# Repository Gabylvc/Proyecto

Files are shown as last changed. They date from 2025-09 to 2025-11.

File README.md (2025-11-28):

# 🧬 Fundamentos de Biodiseño - REMOOV

Este proyecto forma parte del curso **Fundamentos de Biodiseño** del grupo 11.  
A continuación, se presentan los integrantes del equipo de trabajo.

---

##  Integrantes

- **Goran Acurio Cabrera**  - goran.acurio@upch.pe
- **Gabriela Barrios** - gabriela.barrios@upch.pe
- **Jorge Briceño Hijar** - jorge.briceno@upch.pe
- **Marco Baltazar** - marco.baltazar@upch.pe
- **Camila Araujo** - camila.araujo@upch.pe
- **Katherin Berrio** - katherin.berrio@upch.pe

---

## Grupo de trabajo

| Grupo de trabajo|
|--------------|
| foto |

---

## Temática

En este proyecto nos enfocamos en proporcionar una alternativa de movimiento en silla de ruedas para usuarios con lesiones medulares que cuentan con movilidad parcial en las extremidades superiores
|--------------|
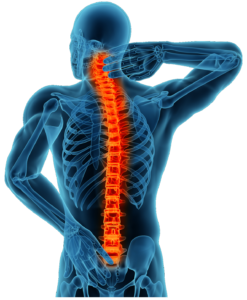
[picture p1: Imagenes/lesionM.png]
foto
|  |
---
## Problemática
El usuario sufrió una lesión medular C4 incompleta tipo C como producto de un accidente automovilístico. A raíz de esta lesión  la movilidad del paciente se encuentra comprometida, dependiendo completamente de una silla de ruedas para desplazarse. Sus extremidades inferiores no tienen rango de movilidad alguna, sin embargo tiene cierto rango de movimiento en sus brazos, lo que llevó a pensar que sería capaz de remar su silla de ruedas, sin embargo al no poder cerrar los dedos de las manos ni poder retraer completamente los brazos se le hizo imposible, por lo que ahora depende completamente de sus cuidadora principal.
## Justificación
Las sillas de ruedas convencionales son ampliamente utilizadas gracias a su bajo costo, disponibilidad y accesibilidad. Sin embargo, existen usuarios con limitaciones en su capacidad motora que requieren asistencia para desplazarse perdiendo su autonomía y desarrollo en actividades cotidianas.
El esfuerzo físico requerido para propulsar una silla mecánica puede resultar excesivo y puede llegar a generar fatiga muscular, lesiones por el sobreuso y desgaste prematuro en articulaciones; muestra de esto es el hecho de que, entre 31-73% de la población con lesiones en la médula espinal reportan dolor de hombro, muchas veces crónico [1]. A ello se le suma la necesidad recurrente de un acompañante, lo que restringe la independencia del usuario y limita su integración plena en la sociedad. 
En el caso específico de nuestro paciente, su limitada movilidad y fuerza en los brazos hace casi imposible el buen manejo de su silla de ruedas, necesidad en la cual nos enfocaremos.
En tal sentido, es necesario buscar alternativas para las sillas de ruedas convencionales, ya que en el mercado ya existen dispositivos motorizados; sin embargo, suelen implicar un costo elevado, dificultades en el mantenimiento y poca adaptabilidad a contextos con recursos limitados.
## Solución
Sistema de propulsión asistida basada en una palanca conectada al sobrearo de la silla de ruedas.
|--------------|
| foto |
---

## Referencias
[1] A. Liampas, P. Neophytou, M. Sokratous, G. Varrassi, C. Ioannou, G. M. Hadjigeorgiou, and P. Zis, “Musculoskeletal Pain Due to Wheelchair Use: A Systematic Review and Meta-Analysis,” Pain Ther., vol. 10, no. 2, pp. 973–984, Dec. 2021, doi: 10.1007/s40122-021-00294-5.

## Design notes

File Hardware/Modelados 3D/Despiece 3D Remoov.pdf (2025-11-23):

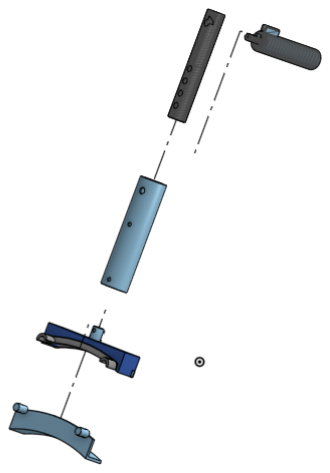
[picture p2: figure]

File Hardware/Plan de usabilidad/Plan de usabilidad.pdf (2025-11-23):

Plan de usabilidad:
a. Contexto de uso
¿Quién es el usuario?
El dispositivo está dirigido a pacientes con lesiones medulares graves que conservan movilidad parcial en las extremidades superiores; además, se cuenta con funciones de monitoreo dirigidas al cuidador y al terapeuta.
¿Cómo se utiliza el dispositivo?
El dispositivo debe acoplarse al sobre aro de la silla de ruedas y ajustarse a ella; después, la altura de la palanca debe ajustarse a la altura óptima para el agarre del usuario. Una vez realizados estos pasos, la electrónica del dispositivo se enciende mediante un switch ubicado en la caja electrónica. El movimiento de la silla de ruedas se logra mediante el movimiento de los brazos del usuario en forma de remo hacia adelante y hacia atrás, de esta manera se logra hacer fricción con el sobre aro y propulsar la silla hacia adelante; para realizar el cambio de adelante hacia atrás, se utiliza un cable bowden, el cual cambia el sentido con un movimiento de giro del mango del usuario.
La aplicación se conecta mediante bluetooth al sistema electrónico del dispositivo; una vez conectado, la información en forma de gráficas de la presión ejercida y el ángulo de movimiento se presentarán en la pantalla.
¿Dónde se utilizará el dispositivo?
El dispositivo está diseñado para que el paciente pueda utilizarlo en cualquier lugar donde se encuentre, ya sea en su hogar, en el hospital o en la calle. Por lo tanto, su frecuencia de uso también es elevada, ya que cubre todos los momentos en los cuales el paciente utiliza su silla de ruedas.

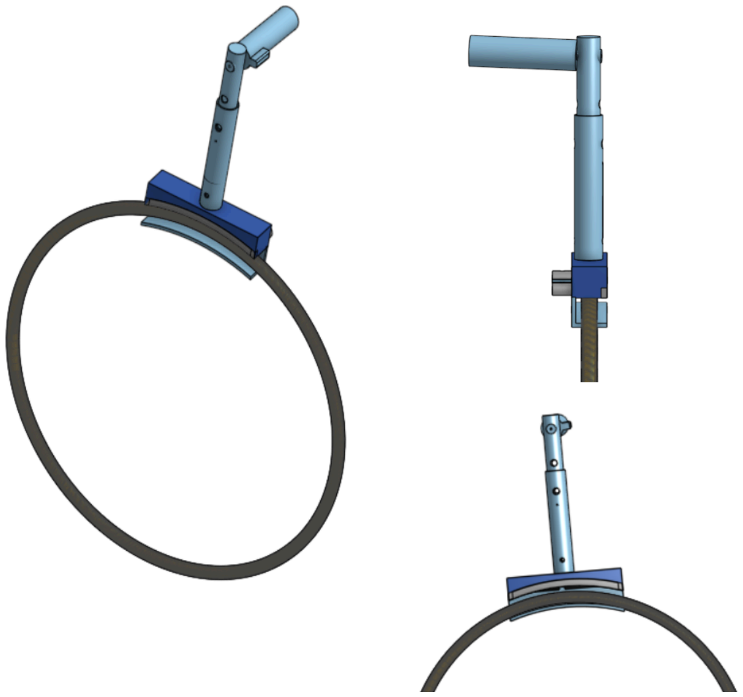
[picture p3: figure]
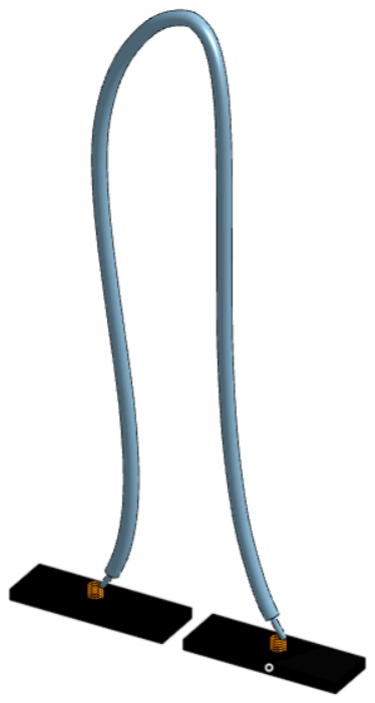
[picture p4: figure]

b. Perfil del usuario

–Qué es:
El usuario es un hombre de 30 años con una lesión medular cervical C3–C4 (AIS C) provocada por un accidente de tránsito. Desde entonces, presenta parálisis total en las piernas y fuerza muy limitada en los brazos. Su movilidad activa está reducida en las cuatro extremidades, aunque conserva sensibilidad hasta el nivel C4. En los brazos apenas logra fuerza entre 4/5 y 1/5, lo que le dificulta propulsar una silla de ruedas convencional. Aun así, mantiene plena conciencia, comprensión y orientación, lo que le permite participar activamente en su proceso de rehabilitación

– Qué hacer:
El paciente necesita un sistema que le permita desplazarse con menor esfuerzo y mayor seguridad. Para ello se propone una palanca de asistencia basada en la patente Wheelchair Propulsion Assist Device (US11590039B1), que se instala sobre el aro de la rueda para reducir el torque necesario y aprovechar la fuerza residual de los brazos. Además, se integra electrónica al diseño: un sensor de fuerza para medir el esfuerzo de propulsión, un giroscopio para registrar la estabilidad del movimiento y una alerta automática conectada a una aplicación móvil que avisa si el usuario sufre una caída o pierde el equilibrio. Este sistema busca facilitar la movilidad, prevenir lesiones en los hombros y aumentar la independencia en sus actividades diarias. [1]

– Qué evidencia debe incluir:
El caso clínico proporciona la información principal sobre el estado físico, diagnóstico y metas de rehabilitación del paciente, que sirven de base para el diseño del dispositivo.La patente US11590039B1 respalda el principio mecánico del sistema de palanca y demuestra su aplicabilidad en sillas de ruedas. Asimismo, estudios científicos como el de Requejo muestran que los mecanismos de palanca reducen la carga muscular en los hombros de personas con lesión medular. [2]

En conjunto, la información clínica, la evidencia técnica y el soporte científico justifican el desarrollo de una palanca asistida con monitoreo electrónico, adaptada a un usuario con severas limitaciones motoras pero con plena capacidad cognitiva, que busca recuperar autonomía y seguridad en su vida cotidiana.

c. Análisis de tareas
Tareas | ¿Crítica? | Riesgos / Consecuencias en caso de error | Justificación
Montar y fijar el dispositivo a la silla de ruedas | Sí | Un desacople mediante el uso de la silla, puede generar una pérdida de control, caída e incluso lesión | Necesidad de un retrofit seguro y puntos de fijación fiables, puesto que un montaje inadecuado compromete la estabilidad y seguridad del usuario [1] [3]

Ajustar y asegurar el agarre (mango) | Sí | Si la mano resbala o se suelta conlleva una pérdida de propulsión y control | Necesario para usuarios con espasticidad o bajo rango de movimiento para transferir fuerza y movimiento a la silla (uso de agarre ergonómico) [3]
Selección de modo (avance / retroceso) | Sí | Movimiento inesperado en el mango o selector mal posicionado ocasionaría colisiones o pérdida de control | Necesidad de definir posiciones de manejo de la silla para evitar movimientos indeseados [1] [4]
Activar freno antes de sentarse / desmontar | Sí | Rodado involuntario provocaría una posible caída del usuario o daños en el dispositivo | Necesidad de mecanismos de bloqueo o freno para evitar rollaway [1] [3] [4]
Realizar gesto de propulsión (remada) | No/ Algunos casos | Mala técnica ocasionaría espasticidad, fatiga, dolor en hombro e incluso riesgo de lesión por sobreuso | Necesidad de un diseño ergonómico para evitar daños por repetición con técnica inadecuada [1] [4]
Monitorear señales / sensores (encender sistema, mantener registro y vigilar alertas) | Sí | Si no hay registro de eventos o alertas, no existe un seguimiento del movimiento de la silla y posibles fallas | Necesidad de detectar situaciones de peligro y un seguimiento del movimiento de la silla para la seguridad del usuario [4]
Desmontaje y almacenamiento | No/ Algunos casos | Un almacenamiento incorrecto provocaría daños en piezas, por lo que el próximo uso sería inseguro | Buenas prácticas de mantenimiento reducen fallas en uso posterior [1] [4]
d. Criterios de éxito:
Criterio | Alcance de objetivo | Método de evaluación
Eficacia | El ≧ 95% de tareas completadas sin error. | Se completó el prototipado electrónico y el modelado en 3D con un correcto indicador de rendimiento. [5]

Eficiencia | < 1 minuto en la inicialización y detección de parámetros. | Cronometrado en las pruebas de desarrollo con un tiempo adecuado para un correcto desarrollo intuitivo. [5]
Satisfacción | Por definir en pruebas con el usuario. | Serie de preguntas durante el uso del dispositivo y evaluado con una métrica SUS [6].
Seguridad | 0 colisiones y fallos críticos | No hubo incidentes durante las pruebas del dispositivo.
Accesibilidad | Contraste ≧ 80%, íconos > 1cm | Se verificó un contraste del 80% y una manipulación sencilla en la aplicación móvil.

Referencias
[1] J. W. Britz, “Wheelchair propulsion assist device,” U.S. Patent 11,590,039 B1, Feb. 28, 2023. [En línea]. Disponible: https://patents.google.com/patent/US11590039B1/en
[2] P. S. Requejo et al., “Shoulder muscular demand during lever-activated vs. pushrim wheelchair propulsion in persons with spinal cord injury,” Arch. Phys. Med. Rehabil., vol. 89, no. 8, pp. 1380–1387, 2008. Available:
https://pubmed.ncbi.nlm.nih.gov/19086715/
[3] D. Zondervan, D. Reinkensmeyer y B. Smith, “Lever-operated wheelchair,” U.S. Patent
9,597,241 | B2, | 21 | de | marzo | de | 2017. | [En | línea]. | Disponible:
https://patents.google.com/patent/US9597241B2/en
[4] P. Bitzer, B. Stumpp, “Dispositivo de asistencia para desplazamiento de silla de ruedas,”
Patente | Española | ES | 2 | 438 | 816 | T3, | 2014. | [En | línea]. | Disponible:
https://patents.google.com/patent/ES2438816T3/es?oq=ES2438816T3
[5] J. Nielsen, Usability Engineering. San Francisco: Academic Press, 1994.
[6] J. Brooke, “SUS: A quick and dirty usability scale,” in Usability Evaluation in Industry, P.
W. | Jordan, | B. | Thomas, | B. | A. | Weerdmeester, | and | I. | L.
https://www.researchgate.net/publication/228593520_SUS_A_quick_and_dirty_usability_sca le (https://www.researchgate.net/publication/228593520_SUS_A_quick_and_dirty_usability_scale)

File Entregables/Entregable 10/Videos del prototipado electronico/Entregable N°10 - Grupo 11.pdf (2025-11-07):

### Entregable N°10 - Grupo 11

Prototipado electrónico:

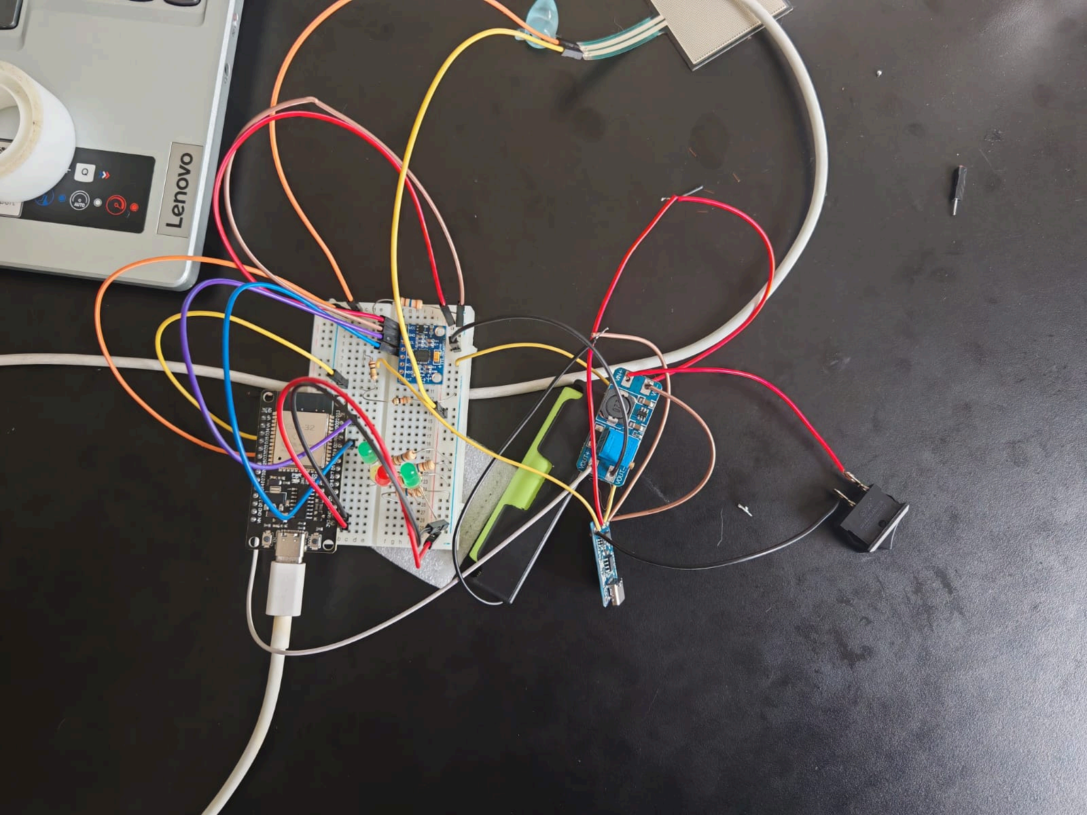
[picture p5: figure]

Videos de funcionamiento:
https://github.com/Gabylvc/Proyecto/tree/main/Entregables/Entregable%2010/Videos %20del%20prototipado%20electronico (https://github.com/Gabylvc/Proyecto/tree/main/Entregables/Entregable%2010/Videos%20del%20prototipado%20electronico)

Animación 3D:
https://drive.google.com/file/d/1b3KnyuPQWc3HMV8ianJPKPj2rIHMH49K/view?usp=drive_link (https://drive.google.com/file/d/1b3KnyuPQWc3HMV8ianJPKPj2rIHMH49K/view?usp=drive_link)

Despiece 3D:

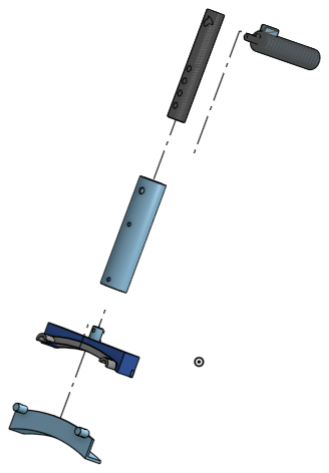
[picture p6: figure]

Plan de usabilidad:
a. Contexto de uso
¿Quién es el usuario?
El dispositivo está dirigido a pacientes con lesiones medulares graves que conservan movilidad parcial en las extremidades superiores; además, se cuenta con funciones de monitoreo dirigidas al cuidador y al terapeuta.
¿Cómo se utiliza el dispositivo?
El dispositivo debe acoplarse al sobre aro de la silla de ruedas y ajustarse a ella; después, la altura de la palanca debe ajustarse a la altura óptima para el agarre del usuario. Una vez realizados estos pasos, la electrónica del dispositivo se enciende mediante un switch ubicado en la caja electrónica. El movimiento de la silla de ruedas se logra mediante el movimiento de los brazos del usuario en forma de remo hacia adelante y hacia atrás, de esta manera se logra hacer fricción con el sobre aro y propulsar la silla hacia adelante; para realizar el cambio de adelante hacia atrás, se utiliza un cable bowden, el cual cambia el sentido con un movimiento de giro del mango del usuario.

La aplicación se conecta mediante bluetooth al sistema electrónico del dispositivo; una vez conectado, la información en forma de gráficas de la presión ejercida y el ángulo de movimiento se presentarán en la pantalla.
¿Dónde se utilizará el dispositivo?
El dispositivo está diseñado para que el paciente pueda utilizarlo en cualquier lugar donde se encuentre, ya sea en su hogar, en el hospital o en la calle. Por lo tanto, su frecuencia de uso también es elevada, ya que cubre todos los momentos en los cuales el paciente utiliza su silla de ruedas.


b. Perfil del usuario

–Qué es:


El usuario es un hombre de 30 años con una lesión medular cervical C3–C4 (AIS C) provocada por un accidente de tránsito. Desde entonces, presenta parálisis total en las piernas y fuerza muy limitada en los brazos. Su movilidad activa está reducida en las cuatro extremidades, aunque conserva sensibilidad hasta el nivel C4. En los brazos apenas logra fuerza entre 4/5 y 1/5, lo que le dificulta propulsar una silla de ruedas convencional. Aun así, mantiene plena conciencia, comprensión y orientación, lo que le permite participar activamente en su proceso de rehabilitación

– Qué hacer:
El paciente necesita un sistema que le permita desplazarse con menor esfuerzo y mayor seguridad. Para ello se propone una palanca de asistencia basada en la patente Wheelchair Propulsion Assist Device (US11590039B1), que se instala sobre el aro de la rueda para reducir el torque necesario y aprovechar la fuerza residual de los brazos. Además, se integra electrónica al diseño: un sensor de fuerza para medir el esfuerzo de propulsión, un giroscopio para registrar la estabilidad del movimiento y una alerta automática conectada a una aplicación móvil que avisa si el usuario sufre una caída o pierde el equilibrio. Este sistema busca facilitar la movilidad, prevenir lesiones en los hombros y aumentar la independencia en sus actividades diarias. [1]

– Qué evidencia debe incluir:
El caso clínico proporciona la información principal sobre el estado físico, diagnóstico y metas de rehabilitación del paciente, que sirven de base para el diseño del dispositivo.La patente US11590039B1 respalda el principio mecánico del sistema de palanca y demuestra su aplicabilidad en sillas de ruedas. Asimismo, estudios científicos como el de Requejo muestran que los mecanismos de palanca reducen la carga muscular en los hombros de personas con lesión medular. [2]

En conjunto, la información clínica, la evidencia técnica y el soporte científico justifican el desarrollo de una palanca asistida con monitoreo electrónico, adaptada a un usuario con severas limitaciones motoras pero con plena capacidad cognitiva, que busca recuperar autonomía y seguridad en su vida cotidiana.

c. Análisis de tareas
Tareas | ¿Crítica? | Riesgos / Consecuencias en caso de error | Justificación
Montar y fijar el dispositivo a la silla de ruedas | Sí | Un desacople mediante el uso de la silla, puede generar una pérdida de control, caída e incluso lesión | Necesidad de un retrofit seguro y puntos de fijación fiables, puesto que un montaje inadecuado compromete la estabilidad y seguridad del usuario [1] [3]
Ajustar y asegurar el agarre (mango) | Sí | Si la mano resbala o se suelta conlleva una pérdida de propulsión y control | Necesario para usuarios con espasticidad o bajo rango de movimiento para transferir fuerza y movimiento a la silla (uso de agarre ergonómico) [3]
Selección de modo (avance / retroceso) | Sí | Movimiento inesperado en el mango o selector mal posicionado ocasionaría colisiones o pérdida de control | Necesidad de definir posiciones de manejo de la silla para evitar movimientos indeseados [1] [4]
Activar freno antes de sentarse / desmontar | Sí | Rodado involuntario provocaría una posible caída del usuario o daños en el dispositivo | Necesidad de mecanismos de bloqueo o freno para evitar rollaway [1] [3] [4]

Realizar gesto de propulsión (remada) | No/ Algunos casos | Mala técnica ocasionaría espasticidad, fatiga, dolor en hombro e incluso riesgo de lesión por sobreuso | Necesidad de un diseño ergonómico para evitar daños por repetición con técnica inadecuada [1] [4]
Monitorear señales / sensores (encender sistema, mantener registro y vigilar alertas) | Sí | Si no hay registro de eventos o alertas, no existe un seguimiento del movimiento de la silla y posibles fallas | Necesidad de detectar situaciones de peligro y un seguimiento del movimiento de la silla para la seguridad del usuario [4]
Desmontaje y almacenamiento | No/ Algunos casos | Un almacenamiento incorrecto provocaría daños en piezas, por lo que el próximo uso sería inseguro | Buenas prácticas de mantenimiento reducen fallas en uso posterior [1] [4]
d. Criterios de éxito:
Criterio | Alcance de objetivo | Método de evaluación
Eficacia | El ≧ 95% de tareas completadas sin error. | Se completó el prototipado electrónico y el modelado en 3D con un correcto indicador de rendimiento. [5]
Eficiencia | < 1 minuto en la inicialización y detección de parámetros. | Cronometrado en las pruebas de desarrollo con un tiempo adecuado para un correcto desarrollo intuitivo. [5]
Satisfacción | Por definir en pruebas con el usuario. | Serie de preguntas durante el uso del dispositivo y evaluado con una métrica SUS [6].
Seguridad | 0 colisiones y fallos críticos | No hubo incidentes durante las pruebas del dispositivo.
Accesibilidad | Contraste ≧ 80%, íconos > 1cm | Se verificó un contraste del 80% y una manipulación sencilla en la aplicación móvil.

Referencias
[1] J. W. Britz, “Wheelchair propulsion assist device,” U.S. Patent 11,590,039 B1, Feb. 28, 2023. [En línea]. Disponible: https://patents.google.com/patent/US11590039B1/en
[2] P. S. Requejo et al., “Shoulder muscular demand during lever-activated vs. pushrim wheelchair propulsion in persons with spinal cord injury,” Arch. Phys. Med. Rehabil., vol. 89, no. 8, pp. 1380–1387, 2008. Available:
https://pubmed.ncbi.nlm.nih.gov/19086715/
[3] D. Zondervan, D. Reinkensmeyer y B. Smith, “Lever-operated wheelchair,” U.S. Patent
9,597,241 | B2, | 21 | de | marzo | de | 2017. | [En | línea]. | Disponible:
https://patents.google.com/patent/US9597241B2/en
[4] P. Bitzer, B. Stumpp, “Dispositivo de asistencia para desplazamiento de silla de ruedas,”
Patente | Española | ES | 2 | 438 | 816 | T3, | 2014. | [En | línea]. | Disponible:
https://patents.google.com/patent/ES2438816T3/es?oq=ES2438816T3
[5] J. Nielsen, Usability Engineering. San Francisco: Academic Press, 1994.
[6] J. Brooke, “SUS: A quick and dirty usability scale,” in Usability Evaluation in Industry, P.
W. | Jordan, | B. | Thomas, | B. | A. | Weerdmeester, | and | I. | L.
https://www.researchgate.net/publication/228593520_SUS_A_quick_and_dirty_usability_sca le (https://www.researchgate.net/publication/228593520_SUS_A_quick_and_dirty_usability_scale)

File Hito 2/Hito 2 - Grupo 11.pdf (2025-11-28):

RE-

# MOOVE

P R E S E N T A C I Ó N

Presentado por: GRUPO 11
FUNDAMENTOS DEL BIODISEÑO

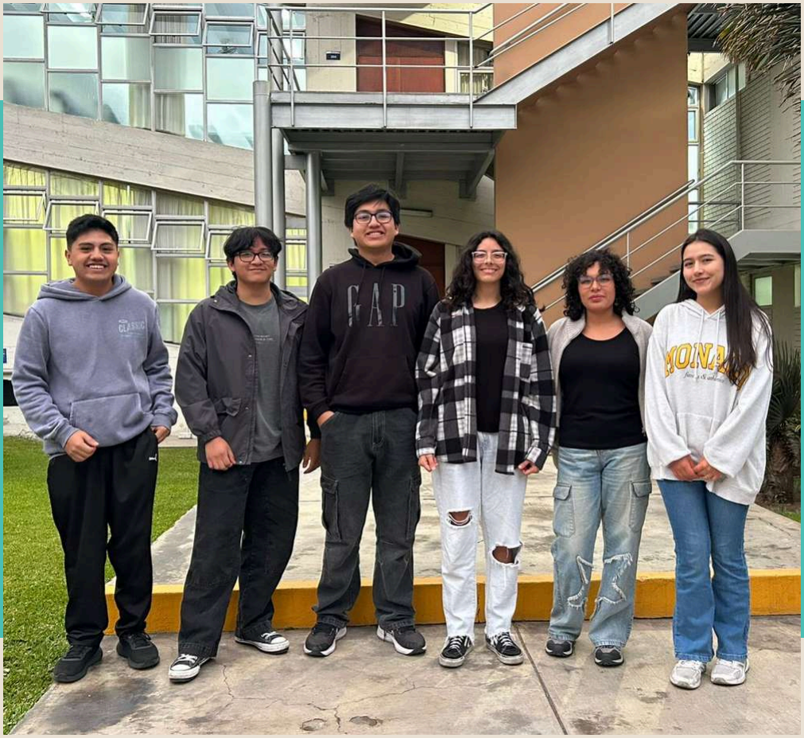
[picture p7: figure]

# El equipo

Goran Acurio (Coordinador y E.

electrónica)
Camila Araujo (E. de Mecanismos) Marco Baltazar (E. de Manufactura

Digital)
Gabriela Barrios (E. de Ensamblado e

integración)
Katherin Berrio (E. de Mecanismos) Jorge Briceño (E. de Diseño Digital)

01

# Problemática y Solución

# Lesión Medular Cervical C3–C5

### Consecuencia:

Tetraparesia → fuerza limitada en hombros, sin control en manos/piernas.

### Zona afectada:

Médula espinal cervical

### Implicaciones:

Pérdida parcial de movilidad y sensibilidad en brazos y piernas.

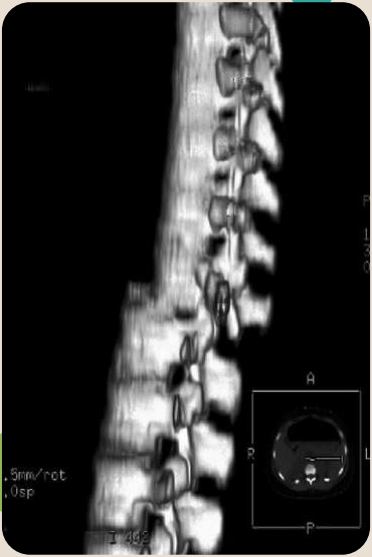
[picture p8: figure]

Lesión Medular Cervical C3–C5: https://www.fisioterapianeurologica.es/patologias/lesion-medular/

# Estadísticas

personas sufren una lesión medular

El INR indica que alrededor del 60 % de los casos se deben a a accidentes vehiculares [2]

Según la Organización Mundial de la Salud...

de casos corresponden 62% a lesiones cervicales. [1]

250000 - 500000

Otras

Accidentes de
tránsito

Caídas

60%

25%

5%

En el Perú...

1

2

3

# Análisis de caso

Problema clínico y funcional:

Fuerza parcial en hombros y ausencia de movimiento en
manos
Dificultad | severa | para
propulsar una silla de ruedas. No puede desplazarse por sí mismo, depende de terceros.

Necesidad del usuario:

Mover la silla con menor esfuerzo y mayor comodidad en su día a día Recibe manejo integral de rehabilitación, incluyendo fisioterapia para mantener el tono muscular; sin embargo, requiere logra propulsión funcional independiente.

Impacto esperado de la solución:

Recuperar autonomía en movilidad. Reducir la dependencia de cuidadores. Facilitar su participación activa en su entorno social, educativo y laboral.

Imagen del caso clínico.
Fuente: Muñoz Maldonado,
C. (2024). Presentación de clase, Rehabilitación.

Análisis biomecánico de propulsión en silla de ruedas.
https://www.frontiersin.org/journals/rehabilit ationsciences/articles/10.3389/fresc.2022.863093 /full

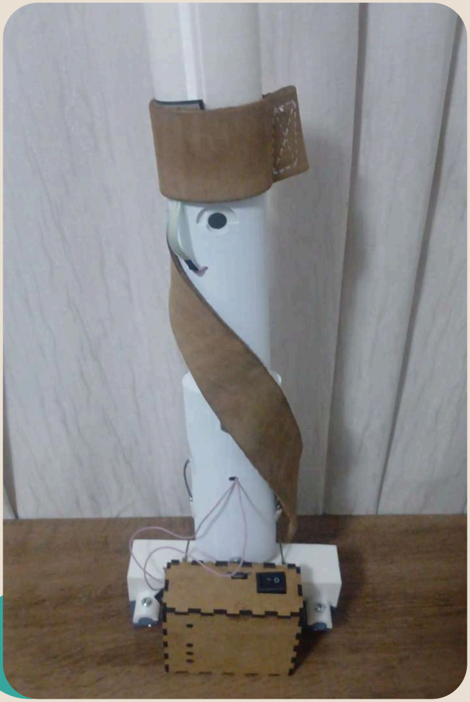
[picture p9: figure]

# SOLUCIÓN ENCONTRADA:

Acoplar el dispositivo en la silla de ruedas Seleccionar el modo avance/retroceso y encender la electrónica si es necesario tomar datos
Realizar movimientos de remo

## “Sistema de propulsión en forma de palanca acoplado al sobrearo

”

02

# Boceto y modelado 3D

# B O C ET O S INI C I A LES

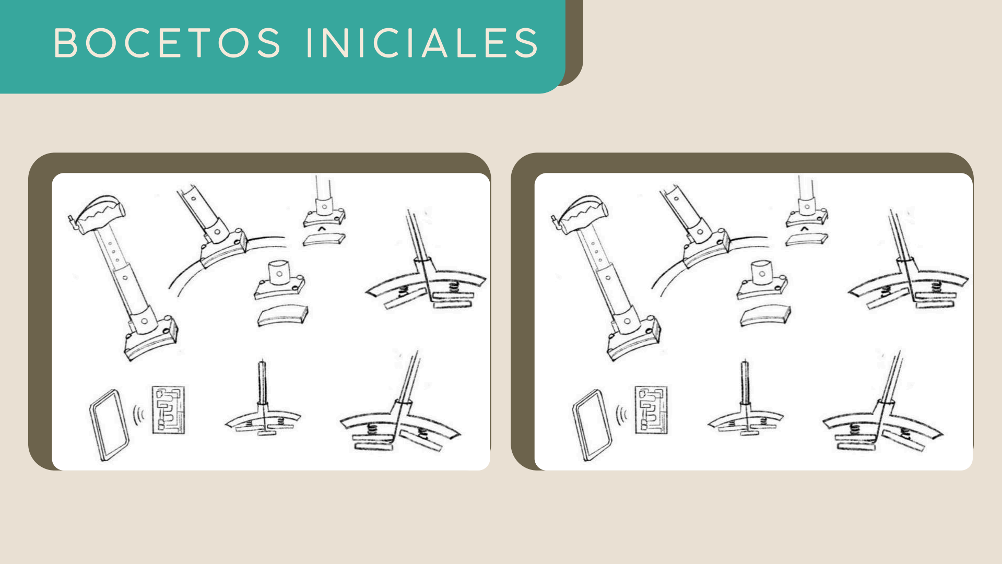
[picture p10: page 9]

# PRIMER A S PIEZ A S

## C A J A DE ELE C TR O NI C A

## P A L ANC A RE GUL A BLE

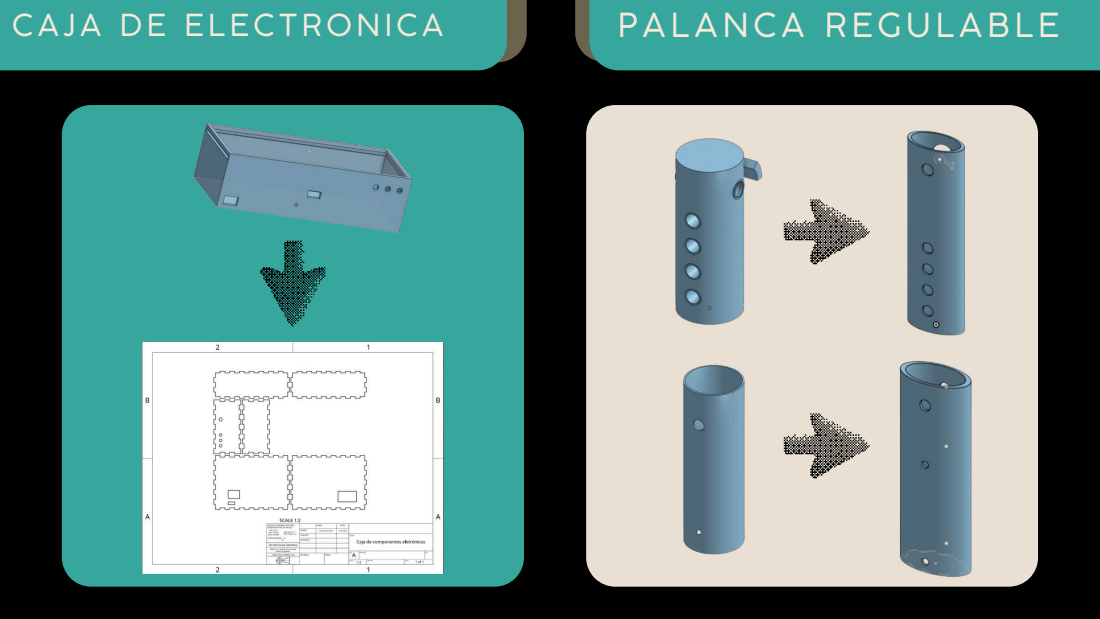
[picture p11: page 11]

MA R C O SUPERI O R | MANG O

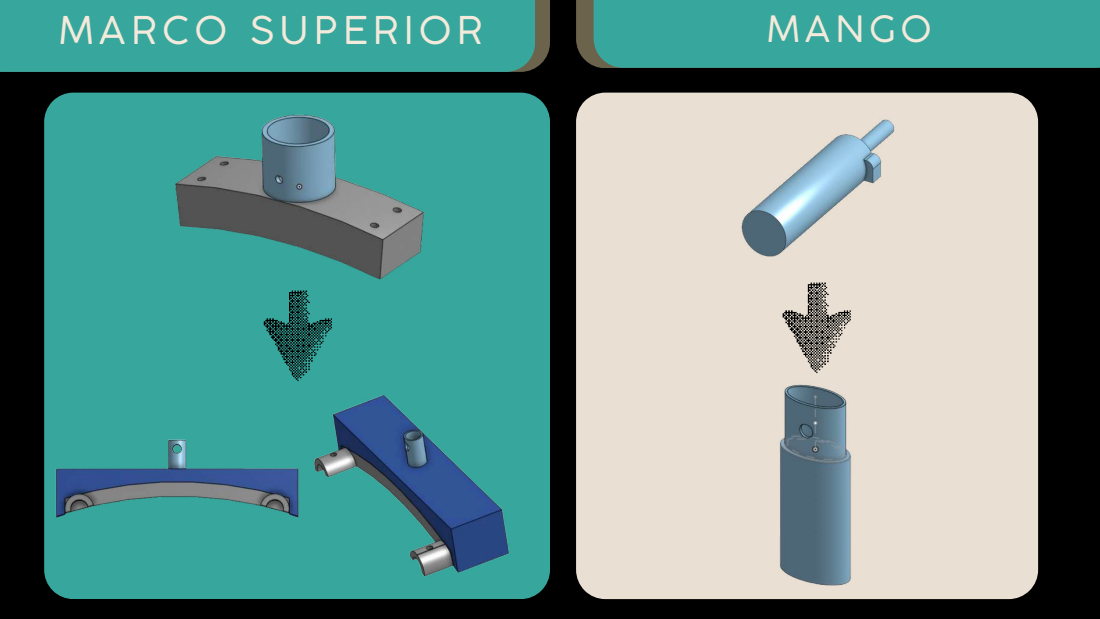
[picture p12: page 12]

# MA R C O INFERI O R

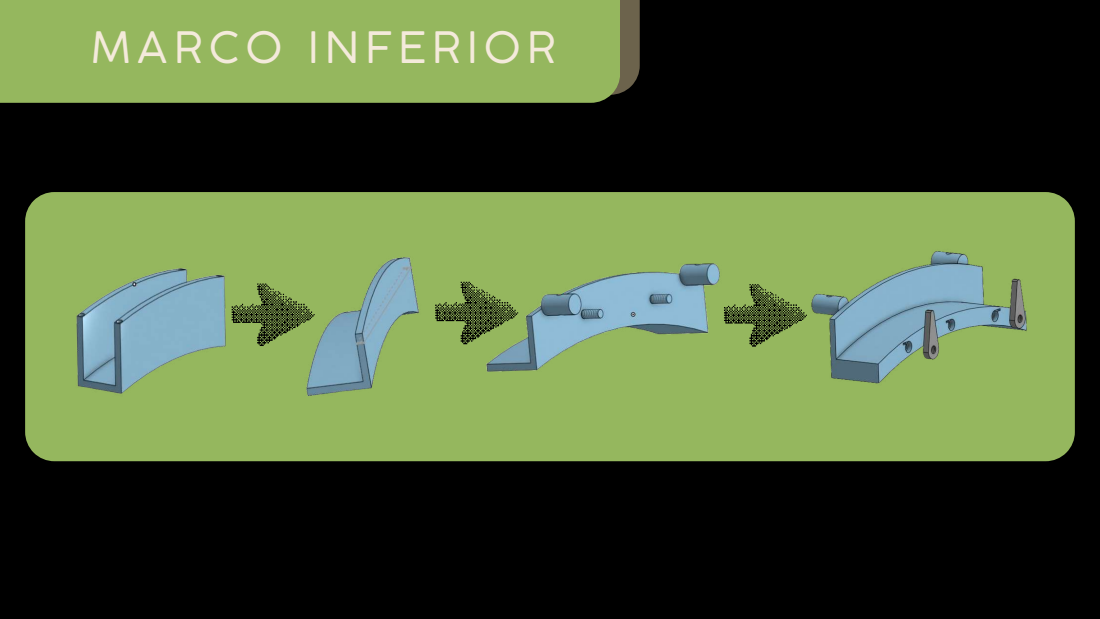
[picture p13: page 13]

# ENS AMBL AD O S 3D

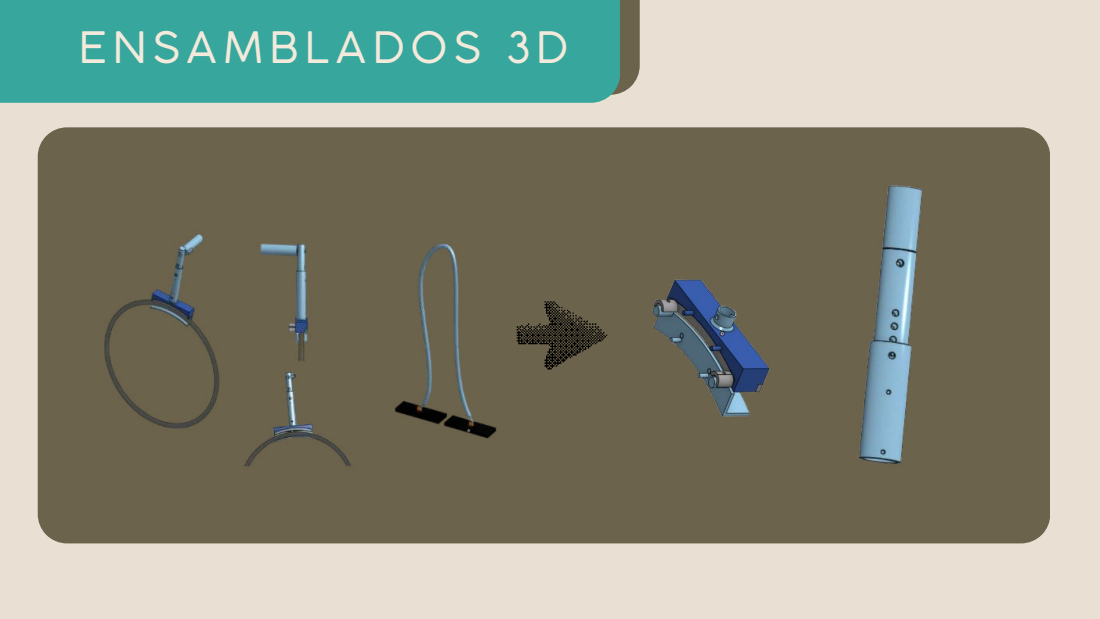
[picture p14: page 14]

# ENS AMBL AD O S 3D

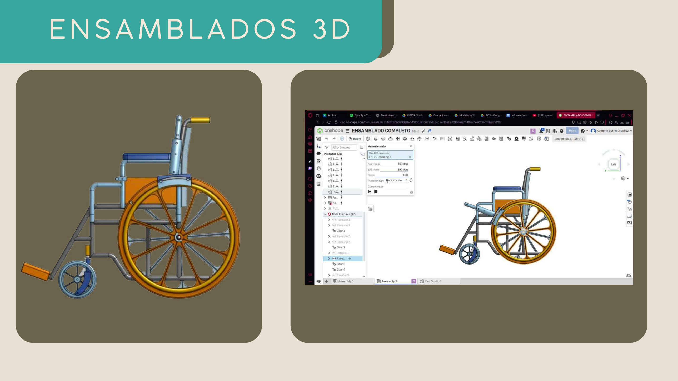
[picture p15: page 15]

03

# Aplicación Movil y Diagrama Electrónico

# A PL I C A C I Ó N MO V I L

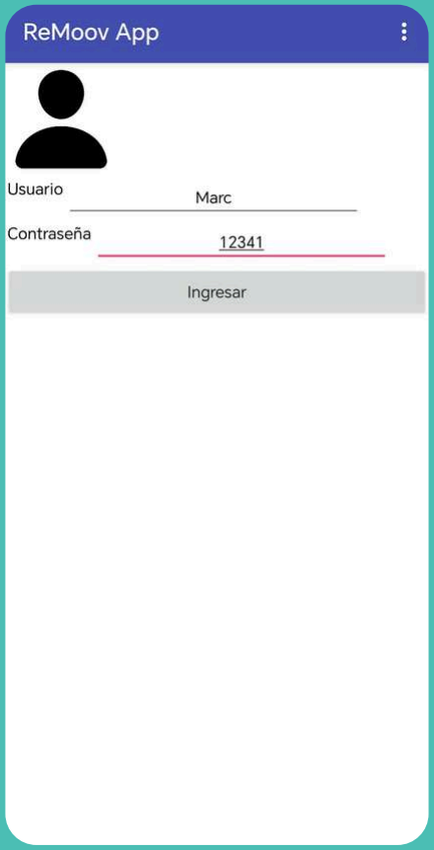
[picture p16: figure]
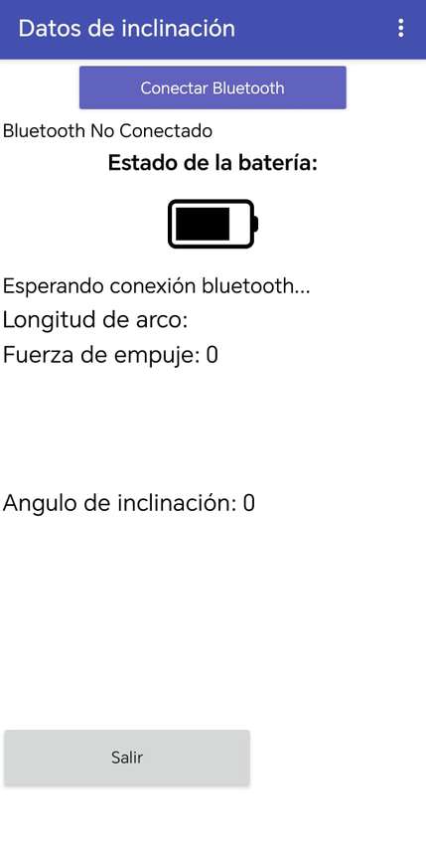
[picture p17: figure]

Pantalla de log-in | Pantalla de Inicio | Recopilación de datos

Recopilación de Datos

# A PL I C A C I Ó N MO V I L

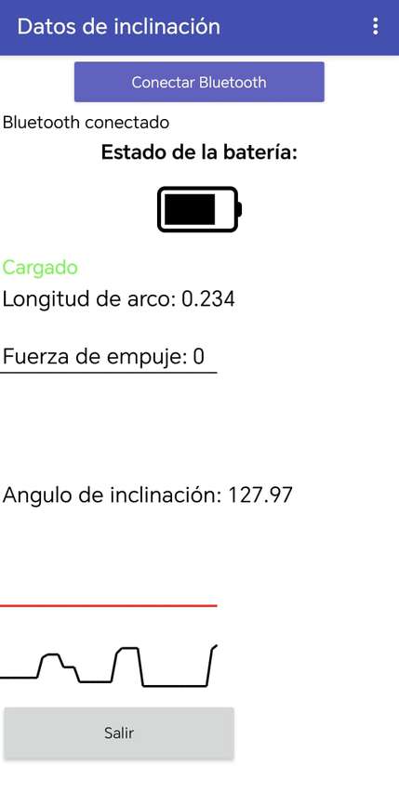
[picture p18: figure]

# DI A G R AMA ELE C TR Ó NI C O

# DI A G R AMA ELE C TR Ó NI C O

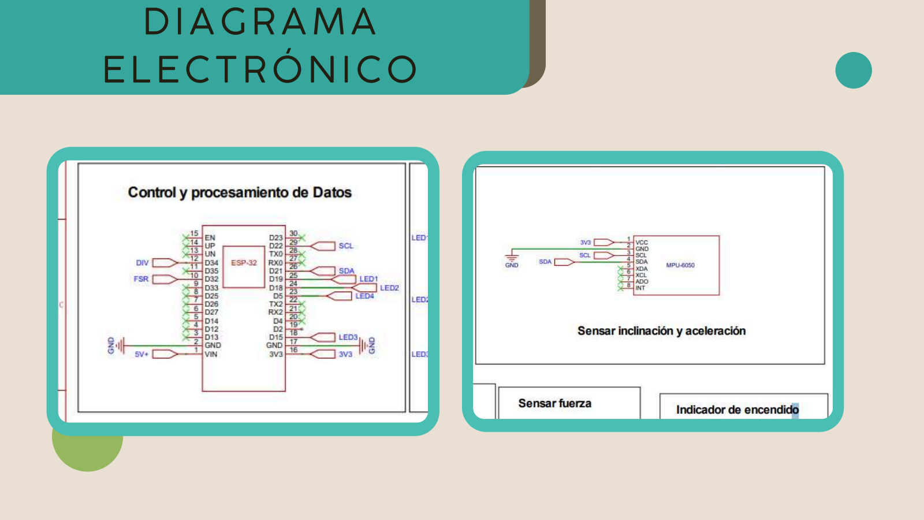
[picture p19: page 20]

# DI A G R AMA ELE C TR Ó NI C O

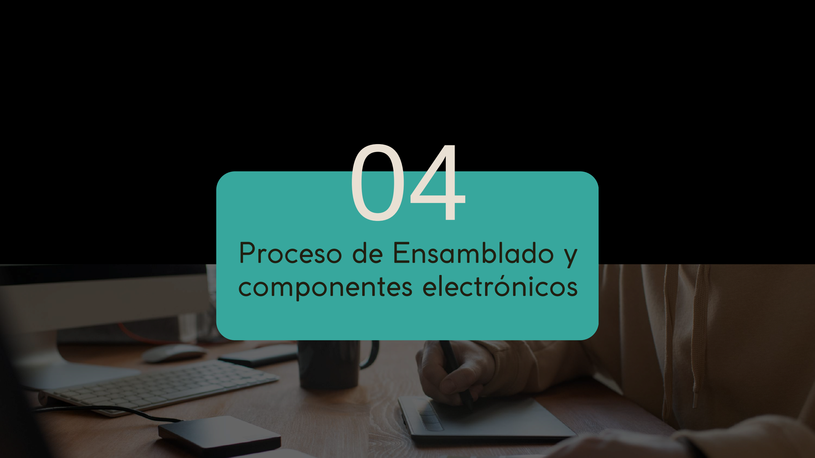
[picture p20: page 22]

04

## Proceso de Ensamblado y componentes electrónicos

# Componentes Electrónicos

ESP32

Step-up

TP4056

MPU6050

Batería Litio 3.7V

FSR406

LEDs

I
m

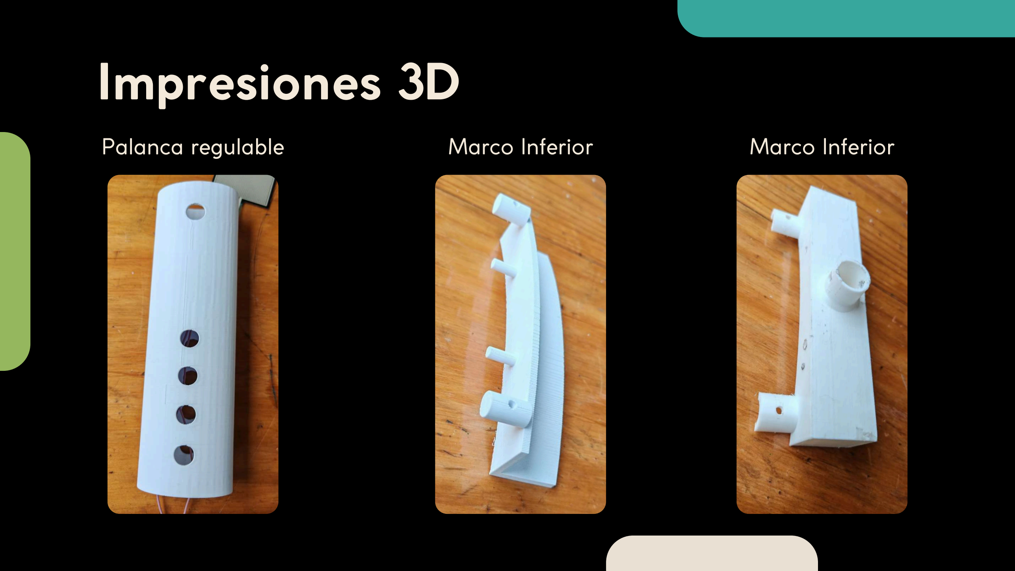
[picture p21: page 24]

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
o In

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
o In

f
e

rio

r

# Integración:

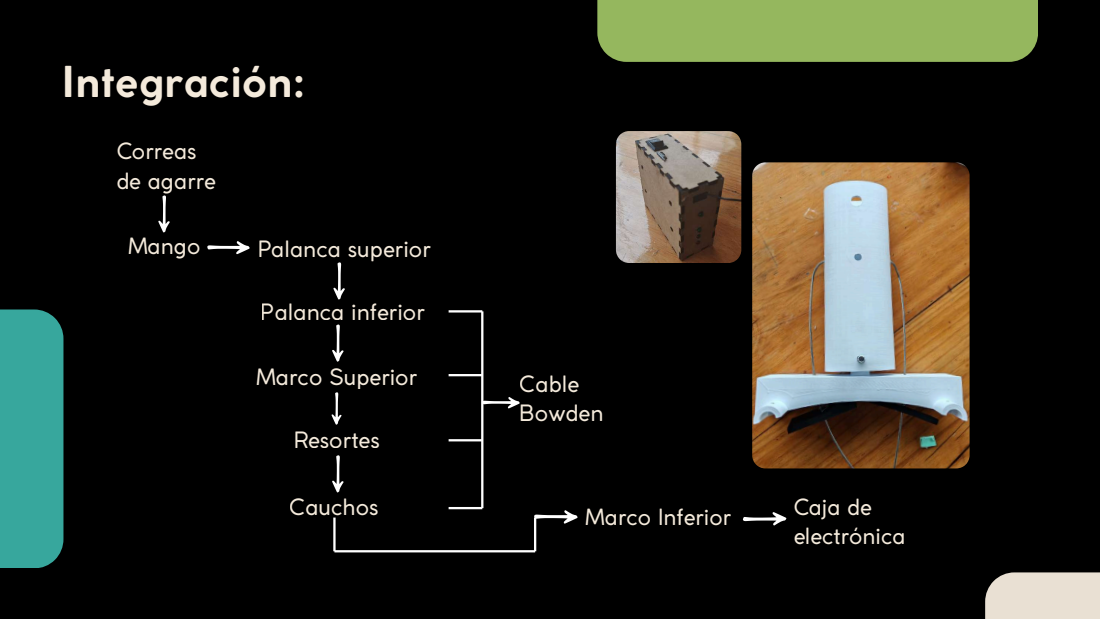
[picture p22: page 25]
Cauchos; Palanca inferior; Correas de agarre; Marco Superior; Caja de electrónica; Palanca superior; Resortes; Mango; Marco Inferior; Cable Bowden

# Proceso de Ensamblado

# Retos Iniciales

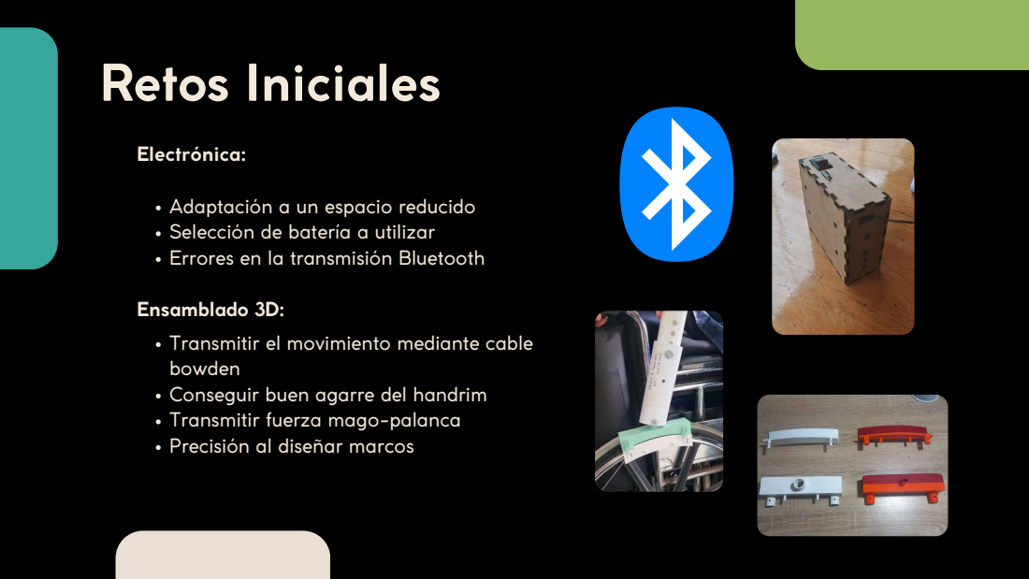
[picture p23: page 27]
Electrónica:

Adaptación a un espacio reducido
Selección de batería a utilizar
Errores en la transmisión Bluetooth

Ensamblado 3D:
Transmitir el movimiento mediante cable
bowden
Conseguir buen agarre del handrim
Transmitir fuerza mago-palanca
Precisión al diseñar marcos

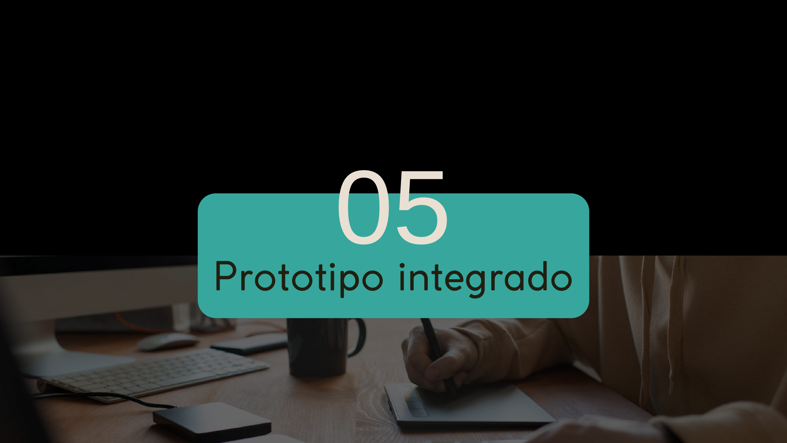
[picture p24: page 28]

05

# Prototipo integrado

## PRIMER Y SE GUND O PR O T O TIP AD O

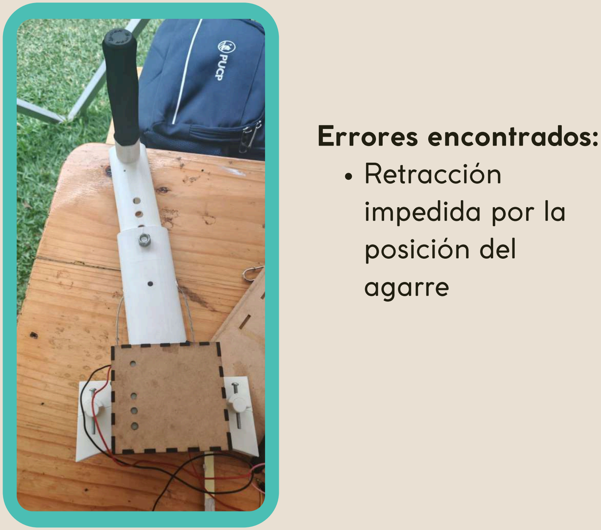
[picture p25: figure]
Errores encontrados: Retracción impedida por la posición del agarre

Errores encontrados:
Retracción del
cable hacia el
centro
Estabilidad en el
sobrearo


# Cambios en Modelado

## TER C ER PR O T O TIP AD O


Soluciones aplicadas:

Cambio de la posición
del agarre
Tope inferior añadido
en el marco inferior
Cables Bowden por
fuera de la palanca

## V IDE O DE FUNC I O NAMIENT O


# 06 Limitaciones y

# trabajo a futuro


Palanca de aluminio
Durabilidad y
resistencia.
Mayor torque en el
movimiento
Más niveles de
graduación

Aplicación móvil
Interfaz con base de
datos.
Registro a largo plazo
para monitorizar al
paciente.

# 07 Pruebas y testeos

## Prueba del mecanismo de cable Bowden

# REFERENC I A S

[1] World Health Organization,
“Lesión de la médula espinal,

” WHO, 16 abril 2024. [En línea]. Disponible: https://www.who.int/es/news-room/fact-sheets/detail/spinal-cordinjury#:~:text=En%20el%20mundo%20hay%20m%C3%A1s,que%20significa%20que%20p ueden%20prevenirse.

[2] Instituto Nacional de Rehabilitación
“Dra. Adriana Rebaza Flores

” AMISTAD PERÚ-JAPÓN, Boletín Epidemiológico Ene 2023 – INR, 3 de marzo de 2023. [En línea]. Disponible: https://www.gob.pe/institucion/inr/informes-publicaciones/3967018-boletinepidemiologico-ene-2023-inr


# Muchas gracias

Grupo 11

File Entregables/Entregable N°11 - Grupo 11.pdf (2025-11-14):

## Entregable N°11 - Grupo 11

1. Verificación de Software: Tabla de verificación:

Verificación de Software
Funcionalidad | Cumplimiento | Observaciones
Si | No
Sensa señales de fuerza de empuje y ángulo de inclinación de movimiento | X | | Es necesario adaptar la posición del sensor de fuerza dentro del agarre ergonómico conseguido
Procesa y transmite datos mediante Bluetooth a una aplicación móvil | X | | La transmisión de Bluetooth se da cada medio segundo, este intervalo es modificable
La aplicación indica el nivel de batería del dispositivo | X | | La aplicación cuenta ahora con 3 pantallas principales (Log-in, Perfil de usuario, Toma de datos)
La aplicación es intuitiva y fácil de utilizar para el usuario (terapeuta/acompañante) | X | | Las funciones de la aplicación pueden ampliarse para generar un espacio de conversación entre acompañante/usuario y terapeuta
La aplicación permite ingresar el dato de la altura a la que se encuentra la palanca | X
La aplicación cuenta un un sistema de log-in para los usuarios | X | | La aplicación está conectada a una hoja de cálculo donde deben registrarse todos los usuarios y contraseñas válidos
La aplicación muestra gráficas claras y útiles sobre la fuerza y la inclinación | X
A partir de los datos registrados, se calcula la longitud de arco del movimiento del brazo del paciente | X | | Se calcula la longitud de arco cada 5 segundos y se muestra en la aplicación
2. Verificación de Hardware
Preguntas clave:
- ¿Cuánto pesa el dispositivo?
- ¿En qué posición y a que altura se encuentra la palanca y el mango con respecto al usuario?
- ¿Qué switches son necesarios para el funcionamiento correcto del dispositivo?
- ¿Cuánto tiempo dura la batería?
- ¿Es necesario utilizar indicadores visuales?

A partir de estas preguntas, se planteó la siguiente tabla de verificación para el Hardware: Tabla de verificación:

Verificación de Hardware
Funcionalidad | Cumplimiento | Test y observaciones
Si | No
El dispositivo tiene una duración de batería mayor a 8 horas | | X | Según una prueba realizada con la batería durante una hora, se determinó que se espera que la batería pueda durar hasta 8 horas; sin embargo, este es un máximo y no se debería utilizar toda la batería durante las 8 horas
Es un dispositivo recargable e indica nivel de batería claramente | X | | La batería es indicada satisfactoriamente mediante 3 LEDs ubicados a un costado de la caja y también mediante la aplicación Web. Hace falta reemplazar uno de los lados de la caja para un encaje mejor de los LEDs
El dispositivo ensamblado en su totalidad tiene un peso menor de 2 kg | X | | El dispositivo pesa aproximadamente 1 kg
El dispositivo cuenta con un switch de ON/OFF | X | | Switch ON/OFF ubicado a un costado de la caja de electrónica
La altura de la palanca del dispositivo es ajustable | X | | Se cuentan con 4 diferentes alturas para la palanca que dependen de la silla de ruedas y del agarre del paciente
El agarre del mango es cómodo y ergonómico | X | | Se ha conseguido una funda para el agarre del mango
El dispositivo cuenta con un mecanismo de cambio de marcha (adelante/retroceso) | Parcialmente | | El mecanismo de cambio de placas de caucho ha sido probado; sin embargo, aun falta adaptar completamente el dispositivo para probar el cambio de marcha
El dispositivo permite al usuario movilizarse en la silla de ruedas | Parcialmente | | Se ha probado que los cauchos de agarre pueden movilizar la silla de ruedas y que el dispositivo sin los cauchos puede deslizar libremente. Aun así, falta integrar completamente el dispositivo para probar el movimiento
El ensamblado de todo el dispositivo toma un tiempo menor a 2 horas | X | | El ensamble de las piezas 3D mediante tuercas y tornillos; junto con la caja electrónica, toma menos de 30 minutos. El integrado de los cables Bowden con los cauchos toma menos de 30 minutos.
El dispositivo puede acoplarse a la silla de ruedas en un tiempo menor a 15 | X | | El ensamble del dispositivo a la silla de ruedas toma menos de 5 minutos

minutos

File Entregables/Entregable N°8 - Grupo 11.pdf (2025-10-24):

## Entregable N°8 - Grupo 11


a. Esquema electrónico de la solución:


b. Modelados de componentes electrónicos:
- Módulo MT 3608


https://cad.onshape.com/documents/4029a7ebfd9528c7b1b792b4/w/bb783dfc386ca368ce65ce2f/e/d3baca16058cdb287b332577 (https://cad.onshape.com/documents/4029a7ebfd9528c7b1b792b4/w/bb783dfc386ca368ce65ce2f/e/d3baca16058cdb287b332577)

- MPU 6050

https://cad.onshape.com/documents/ec0058a47e16e98accb219bd/w/4809cf10cb36dfc7e1e1bffd/e/7e09f68b99f0aa957cbee3c1 (https://cad.onshape.com/documents/ec0058a47e16e98accb219bd/w/4809cf10cb36dfc7e1e1bffd/e/7e09f68b99f0aa957cbee3c1)


- ESP32

https://cad.onshape.com/documents/7b133f08326abbb148e0c937/w/c08abd86d1717b00bf35be89/e/73a5fb76e264edd8f36b6793 (https://cad.onshape.com/documents/7b133f08326abbb148e0c937/w/c08abd86d1717b00bf35be89/e/73a5fb76e264edd8f36b6793)

- Módulo TP4056

https://cad.onshape.com/documents/8dac967d7395424ce5ba9a42/w/2ec2420eda60c145231733ee/e/40dcc385c61f7fa680875e28?renderMode=0&uiState=68fa51d 7b81173cae62f127c (https://cad.onshape.com/documents/8dac967d7395424ce5ba9a42/w/2ec2420eda60c145231733ee/e/40dcc385c61f7fa680875e28?renderMode=0&uiState=68fa51d7b81173cae62f127c)

- Protoboard


https://cad.onshape.com/documents/2d3b330a1e7218b2d0cf7d56/w/8685cd6fe1fd0d0afa3cc885/e/99f3d4a16a6dee5e58b24717?renderMode=0&uiState=68fa50d93 d09582aa8bc0b0c (https://cad.onshape.com/documents/2d3b330a1e7218b2d0cf7d56/w/8685cd6fe1fd0d0afa3cc885/e/99f3d4a16a6dee5e58b24717?renderMode=0&uiState=68fa50d93d09582aa8bc0b0c)

- Batería Li-ion


https://cad.onshape.com/documents/57874c1e8942d4a53ae62745/w/5c973371d1204fd44489d0b4/e/b39cf2b4a4111b4d54e02063?renderMode=0&uiState=68fa5158 ad2acac884811dab (https://cad.onshape.com/documents/57874c1e8942d4a53ae62745/w/5c973371d1204fd44489d0b4/e/b39cf2b4a4111b4d54e02063?renderMode=0&uiState=68fa5158ad2acac884811dab)

- Luz LED


https://cad.onshape.com/documents/3699b5ab19d034abb6495021/w/ee625ca248b2e5beb131fcf7/e/4b81ebe2f528f4fc9cda4674?renderMode=0&uiState=68fa8dd17f3ad056919cd b23 (https://cad.onshape.com/documents/3699b5ab19d034abb6495021/w/ee625ca248b2e5beb131fcf7/e/4b81ebe2f528f4fc9cda4674?renderMode=0&uiState=68fa8dd17f3ad056919cdb23)

- Switch ON/OFF


https://cad.onshape.com/documents/891d18bd603dfe23531a4aa9/w/d4f42a1e21768dab3a62e97a/e/18de39994cf2438b997edd64?renderMode=0&uiState=68fa8f2fc20a4e42bf74c fc5 (https://cad.onshape.com/documents/891d18bd603dfe23531a4aa9/w/d4f42a1e21768dab3a62e97a/e/18de39994cf2438b997edd64?renderMode=0&uiState=68fa8f2fc20a4e42bf74cfc5)

c. Modelados de las partes del dispositivo:
- Caja de componentes electrónicos (v1)


https://cad.onshape.com/documents/66d74b27d3619607c111c88f/w/2e7cd3ca43d23a0913433c67/e/8c2c23deea14621d061e9974?renderMode=0&uiState=68fa52abe02 a657a3752f00d (https://cad.onshape.com/documents/66d74b27d3619607c111c88f/w/2e7cd3ca43d23a0913433c67/e/8c2c23deea14621d061e9974?renderMode=0&uiState=68fa52abe02a657a3752f00d)

- Palanca externa (v1)

https://cad.onshape.com/documents/312285911a13948fd6a4f75c/w/472fcf70584e182bfea51b98/e/d0240779e81f7f0e3da196f3 (https://cad.onshape.com/documents/312285911a13948fd6a4f75c/w/472fcf70584e182bfea51b98/e/d0240779e81f7f0e3da196f3)

- Palanca interna regulable (v1)


https://cad.onshape.com/documents/312285911a13948fd6a4f75c/w/472fcf70584e182bfea51b98/e/3ebe4b685c1b09bab871ce78 (https://cad.onshape.com/documents/312285911a13948fd6a4f75c/w/472fcf70584e182bfea51b98/e/3ebe4b685c1b09bab871ce78)

- Manillar de palanca: (v1)


https://cad.onshape.com/documents/312285911a13948fd6a4f75c/w/472fcf70584e182bfea51b98/e/830ce78cd1304d153ae67e68 (https://cad.onshape.com/documents/312285911a13948fd6a4f75c/w/472fcf70584e182bfea51b98/e/830ce78cd1304d153ae67e68)

- Cobertor del manillar (v1)

https://cad.onshape.com/documents/c30922c880e3c42b98e3a306/w/3196dc4e5192bba2afdbe885/e/0e4809095187ad431300ebf7 (https://cad.onshape.com/documents/c30922c880e3c42b98e3a306/w/3196dc4e5192bba2afdbe885/e/0e4809095187ad431300ebf7)

- Marco en C (2)


https://cad.onshape.com/documents/4ed6db644f42a3677aa62aa7/w/e576891bd8dff6c33bc4092c/e/691bd47b5b1b32eab922c977?renderMode=0&uiState=68faac47f2b b57b903e8ade8 (https://cad.onshape.com/documents/4ed6db644f42a3677aa62aa7/w/e576891bd8dff6c33bc4092c/e/691bd47b5b1b32eab922c977?renderMode=0&uiState=68faac47f2bb57b903e8ade8)

-Mecanismo Interno:

https://cad.onshape.com/documents/46d9706a421488ea0536d395/w/141e5e96b8dc31a0eef05860/e/b560f1952be36f2afecad66a?renderMode=0&uiState=68fadd7aad2 acac88483e010 (https://cad.onshape.com/documents/46d9706a421488ea0536d395/w/141e5e96b8dc31a0eef05860/e/b560f1952be36f2afecad66a?renderMode=0&uiState=68fadd7aad2acac88483e010)

- Marco en C (1)


https://cad.onshape.com/documents/ec4d0679214404f7d9f152c7/w/eeeba341a6782dd9a8463333/e/07f44ee08949e7967a711e6f?renderMode=0&uiState=68faed22136c3e6cc8e5742b (https://cad.onshape.com/documents/ec4d0679214404f7d9f152c7/w/eeeba341a6782dd9a8463333/e/07f44ee08949e7967a711e6f?renderMode=0&uiState=68faed22136c3e6cc8e5742b)

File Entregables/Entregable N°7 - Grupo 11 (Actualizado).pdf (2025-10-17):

### Entregable N°7 - Grupo 11


Checkpoint 3 – Architecture
a. Modelos y principios de solución
- Esquema de funciones

Fig. 1. Esquema de funciones
- Matriz morfológica


Solución A: Primera opción a realizar (color rojo)
Solución B: Segunda opción (color azul)
- Tabla de valoración
Solución | Solución A | Solución B
Principales subfunciones | Criterios
1 | Ajustar el agarre | Usabilidad / Ergonomía | 4 | 3
2 | Seleccionar el modo de movimiento | Eficiencia funcional / Seguridad | 4 | 2
3 | Transmitir movimiento del usuario | Eficiencia / Simplicidad | 3 | 3
4 | Frenar silla de ruedas | Seguridad / Fiabilidad | 3 | 4
5 | Regular energía | Control / Seguridad | 4 | 3
6 | Energizar | Accesibilidad / Independencia | 3 | 3
7 | Sensar fuerza aplicada | Eficiencia / Escalabilidad | 3 | 4
8 | Sensar aceleración del movimiento | Seguridad / Control | 4 | 3

9 | Sensar ángulo de inclinación | Seguridad / Fiabilidad | 4 | 2
10 | Detectar situación de peligro | Seguridad / Fiabilidad | 3 | 3
11 | Controlar interfaz del usuario | Usabilidad / Integración | 4 | 3
12 | Señalizar dispositivo encendido | Seguridad / Usabilidad | 3 | 3
13 | Señalizar situación de peligro | Seguridad / Fiabilidad | 4 | 3
14 | Recopilar e identificar datos | Integración / Escalabilidad | 4 | 3
SUMATORIA | | | 50 | 42
b. Espacio de solución

Dibujado por: Goran Acurio

Boceto en conjunto:


Descripción funcional: El boceto representa toda la solución en su conjunto. Una palanca acoplada al sobrearo de la silla de ruedas con un mango para el agarre del usuario. En el sobrearo se encuentra un mecanismo de agarre con fricción para transmitir el movimiento hacia adelante y soltar al retroceder la palanca | Lista de despiece:
Pieza | Nombre | Material
1 | Palanca | Aluminio
2 | Mango | PLA
3 | Placa deslizante | Aluminio / PLA

4 | Estructura canal

Aluminio

Dibujado por: Goran Acurio

Boceto en conjunto:


Descripción funcional: El boceto representa una vista aumentada de la placa deslizante. En esta se muestra la forma interior la cual se acopla al sobrearo y el material de fricción de recubrimiento | Lista de despiece:
Pieza | Nombre | Material
1 | Placa deslizante | Aluminio /PLA
2 | Material de fricción | Caucho

Dibujado por: Goran Acurio

Boceto en conjunto:


Descripción funcional:
El boceto representa una vista aumentada del mango del dispositivo, el cual cuenta con un forro de material suave para el agarre del usuario y una correa elástica para asegurar el agarre.
| Lista de despiece:
Pieza | Nombre | Material
1 | Mango | PLA
2 | Recubrimient o del mango | Goma TPR
3 | Correa elastica | Velcro
4 | Palanca | Aluminio

c. ¿Fabricar o adquirir?
Componentes | Función en el sistema | Fabricado / Adquirido | Método / fuente | Material / tecnología
Estructura canal en forma de C | Alojar aro de rueda y soportar mecanismo interno | Fabricado | Corte láser , soldadura, montaje. | Aluminio
Palanca telescópica (2) | Palancas ajustables que el usuario empuja | Fabricado | Corte láser , soldadura, montaje. | Aluminio
Mango ergonómico (2) | Superficie de agarre para manipular la palanca telescópica y palanca de cambio | Fabricado | Impresión 3D / Corte láser | PLA/ TPU / Aluminio tubular
Funda de mango ergonómico (2) | Funda Ergonómica para agarre cómodo de los mangos. | Adquirido | ● https://w ww.vent asortope diawong .pe/prod ucto/rep uesto-ba ston-can adiense-comfort (https://www.ventasortopediawong.pe/producto/repuesto-baston-canadiense-comfort) ● https://bi cifixperu .com/pro duct/ma ngos-erg onomico s/ (https://bicifixperu.com/product/mangos-ergonomicos/) | ● Espuma EVA ● Goma TPR
Correas de agarre | Asegurar la mano del usuario para un mejor agarre | Adquirido | ● https://w ww.elect romania. pe/produ cto/corre a-de-vel cro-auto adhesiva -con-heb illa-20x3 00mm/ (https://www.electromania.pe/producto/correa-de-velcro-autoadhesiva-con-hebilla-20x300mm/) | ● Velcro ● Velcro acolchad o

- https://w
ww.otto
bock.co
m/es-es/
product/
29Y63-6
2447 (https://www.ottobock.com/es-es/product/29Y63-62447)
- https://la
casadela
buelo.pe
/product
o/correa-universa
l-para-ut
ensilios/ (https://lacasadelabuelo.pe/producto/correa-universal-para-utensilios/)
- https://la
casadela
buelo.pe
/product
o/correa-universa
l-para-ut
ensilios/ (https://lacasadelabuelo.pe/producto/correa-universal-para-utensilios/)
Láminas de material flexible (2) | Elemento de agarre que genera fricción en los aros de rueda | Adquirido | https://mringenieriasac.com/producto/caucho-ni trilo-nbr (https://mringenieriasac.com/producto/caucho-nitrilo-nbr) | Caucho de nitrilo NBR
Placa deslizante | Soporta / Expone láminas flexible | Fabricado | Corte láser | Aluminio
Carril de placa deslizante | Estructura que guía el movimiento lateral de la placa deslizante con incluye topes que limitan su recorrido | Fabricado | Impresión 3D / Corte láser | PLA/ TPU / Aluminio
Cable bowden | Transmisión desde palanca de cambio a placa deslizante | Adquirido | ● https://m odasa.pe /cable-b owden-d e-8-linea s-r06elv (https://modasa.pe/cable-bowden-de-8-lineas-r06elvw0018.html) | Cable acero + funda Bowden

w0018.h
tml?srslt
id=Afm
BOoqZT
1fsW2O
bjqpig9
Ch_WAf
ju2-WS5
X3am1
DgkiuV
pxJ37M
KrCA (https://modasa.pe/cable-bowden-de-8-lineas-r06elvw0018.html)
- https://e
quiposin
dustriale
s.pe/sho
p/6-431-
258-0-ca
ble-bow
den-acci
onamien
to-de-tra
ccion-ka
rcher-12
913?srslt
id=Afm
BOookx
f67hpbD
79sgCfX
BjlwKu
4hxa25
QM5Bh
A5fSYIl
Fbeqqo
KgB (https://equiposindustriales.pe/shop/6-431-258-0-cable-bowden-accionamiento-de-traccion-karcher-12913)

Palanca de
cambio en
mango

Usuario
selecciona Avance /

Neutral

/
Retroceso
Adquirido | https://gpc.pe/pr oducts/switch-in terruptor-palanc a-4-patas-on-off ?pr_prod_strat= e5_desc&pr_rec _id=e97ead5c1 &pr_rec_pid=8
| 556826689705 &pr_ref_pid=85 56820496553& pr_seq=uniform (https://gpc.pe/products/switch-interruptor-palanca-4-patas-on-off?pr_prod_strat=e5_desc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)

Plástico, cobre

Tornilleria | Fijación general de conjunto | Adquirido
Cubiertas protectoras (PD y cables) | Estética, evitar enganches de ropa y proteger cable | Fabricado | Impresión 3D / Corte láser | PLA/ TPU / Aluminio tubular
Eje | Eje de pivote y unión con canal en C (mecanismo principal) | Fabricado | Corte laser , soldadura | Acero o aluminio
d. Secuencia de procesos
d.1. Montaje del dispositivo:
En primer lugar se debe colocar la silla en una posición estable con los frenos activados. Luego comprobar que el dispositivo se encuentre fijado a los puntos de anclaje del marco principal de la silla. Después colocar al usuario correctamente en el asiento, con una postura adecuada (espalda recta, pies apoyados y cinturón de seguridad). Por último ajustar la altura y ángulo de los mangos o palancas según las dimensiones del usuario a un rango de movimiento cómodo sin sobrecargar sus articulaciones.
d.2. Calibración del sistema:
Para la seguridad del usuario se deben verificar las siguientes partes del dispositivo:
- Mecanismo de propulsión:
Revisar la conexión del sistema de tracción formado por la cinta de fricción y su funcionamiento con el resto del mecanismo. Asegurarse que el mecanismo permita avanzar y retroceder la silla sin complicaciones.
- Ajuste de fricción mecánica:
Se debe regular manualmente la tensión en el punto de anclaje sin causar un movimiento brusco al usuario al momento de su uso.
Además se recomienda una prueba inicial para supervisar el movimiento de la silla de forma estable y segura.
d.3. Sesión de terapia:
El funcionamiento del dispositivo es sencillo, basado en un movimiento tipo “remo”, similar al mecanismo de propulsión de una silla de ruedas mecánica convencional. Durante su uso, un terapeuta puede brindar asistencia y supervisión, orientando al usuario en aspectos como la postura corporal, la simetría del esfuerzo y el rango de movimiento articular, además de planificar sesiones progresivas que favorezcan la adaptación física y el fortalecimiento del paciente.
d.4. Desmontaje:

El sistema puede retirarse fácilmente mediante el desmontaje de los módulos y las palancas de propulsión. Una vez completado el proceso, los componentes deben guardarse en su estuche de almacenamiento, garantizando su protección y conservación para futuros usos. d.5. Limpieza y mantenimiento:
Mantener el dispositivo limpio para prevenir el desgaste de sus componentes. Se recomienda secarlo completamente antes de su guardado, verificar periódicamente el sistema mecánico y lubricar los puntos de fricción. Además, dado que varias piezas están fabricadas mediante impresión 3D, estas pueden sustituirse fácilmente en caso de daño o deformación, garantizando así la continuidad del uso y la durabilidad del sistema.

-Diagrama de flujo:
Para el uso adecuado del dispositivo, el paciente debe seguir el siguiente diagrama de flujo:


Fig. 2. Diagrama de flujo del dispositivo (Fuente: elaboración propia).

e. Técnicas de producción
Componente | Material | Técnica de producción | Justificación
Estructura canal en forma de C | Aluminio | Corte láser y soldadura en aluminio | El corte láser permite precisión en los detalles de la geometría del componente. La soldadura ofrece uniones fuertes y duraderas. El aluminio otorga rigidez, durabilidad y ligereza.
Palanca telescópica (2) | Aluminio | Corte láser y soldadura en aluminio | El corte láser permite precisión en los detalles de la geometría del componente. La soldadura ofrece uniones fuertes y duraderas. El aluminio otorga rigidez, durabilidad y ligereza.
Mango ergonómico (2) | PLA/ TPU / Aluminio tubular | Impresión 3D (TPU / PLA) | La impresión 3D permite manejar con mucho cuidado los detalles de diseño permitiendo personalizar la pieza según la anatomía del usuario.
Placa deslizante | Aluminio | Corte láser en aluminio | El corte láser permite precisión en los detalles de la geometría del componente. El aluminio otorga rigidez, durabilidad y ligereza
Carril de placa | PLA/ TPU / | Impresión 3D, corte | La impresión 3D

deslizante | Aluminio | laser | permite manejar con mucho cuidado los detalles de diseño en geometrías complejas y precisas. El corte láser permite precisión en los detalles de la geometría del componente. El PLA y TPU reducen el peso y los costos, mientras que el aluminio ofrece rigidez.
Cubiertas protectoras (PD y cables) | PLA/ TPU / Aluminio tubular | Impresión 3D/ Corte laser | La impresión 3D permite fabricar cubiertas adaptadas a la forma del mecanismo, protegiendo cables y evitando enganches. El PLA ofrece un diseño personalizado del componente, el TPU ofrece flexibilidad.
Eje | Acero o aluminio | Corte láser y mecanizado | El mecanizado asegura la alineación y ajuste exacto de las partes móviles. El corte láser permite precisión en los detalles de la geometría del componente. Los materiales mecánicos proporcionan durabilidad y resistencia a la corrosión.
f. Estaciones de trabajo

El dispositivo puede utilizarse en entornos cotidianos con superficies regulares, en el cual el usuario realiza sus desplazamientos habituales. También es necesario realizar pruebas de funcionalidad o sesiones de entrenamiento inicial en instituciones de terapia física con la monitorización de un especialista. Adicionalmente, previo a su uso se debe verificar el estado mecánico del sistema y realizar una limpieza básica para garantizar su funcionamiento y seguridad.
g. Automatización
Nivel de automatización: Nivel medio → semiautónomo.
El dispositivo es un accesorio mecánico acoplable a sillas de ruedas convencionales, diseñado para facilitar el movimiento mediante palancas. Aunque su funcionamiento es manual, el uso inicial se realizará bajo supervisión de un fisioterapeuta. Aunque el usuario controla directamente las palancas, la intervención y ajuste del terapeuta permiten adaptar el sistema a las capacidades del paciente y garantizar un uso seguro.

Justificación técnica y clínica:
El nivel medio se justifica porque, aunque el dispositivo no posee componentes electrónicos ni automatizados, su implementación requiere asistencia y supervisión profesional. Está diseñado para personas con movilidad limitada en los brazos, que no pueden girar las ruedas de manera convencional.
El sistema de palancas facilita la propulsión con menor esfuerzo, y los mecanismos de freno y retroceso ofrecen un mayor control en el desplazamiento. Clínicamente, esto favorece la rehabilitación activa y segura, al permitir que el paciente participe en el movimiento, mientras el terapeuta ajusta la intensidad o técnica según el progreso.

Escenarios de seguridad:

- Si el paciente se desmaya o pierde el control: el terapeuta puede intervenir rápidamente y accionar el freno mecánico para detener la silla.
- Si ocurre un fallo mecánico: el dispositivo puede desacoplar fácilmente de la rueda, permitiendo que la silla funcione de forma convencional.
- Protocolo de emergencia: el freno manual cumple la función de parada inmediata. Se ubicará en una zona accesible para el usuario o el terapeuta, garantizando una respuesta rápida ante cualquier situación.
h. Interfaz de red global
El sistema no incorpora electrónica ni conectividad, siendo un dispositivo completamente mecánico. No utiliza sensores, controladores ni transmisión de datos. Por tanto:
- No se recolectan datos fisiológicos ni de desempeño.
- No se requiere conexión a red ni software.
- No se almacenan datos personales ni clínicos.

El enfoque se centra en la interacción física entre el usuario, el dispositivo y el terapeuta, priorizando la ergonomía, seguridad y accesibilidad. Su diseño mecánico permite una implementación práctica en entornos con recursos limitados, manteniendo una función semi autónoma bajo supervisión profesional.

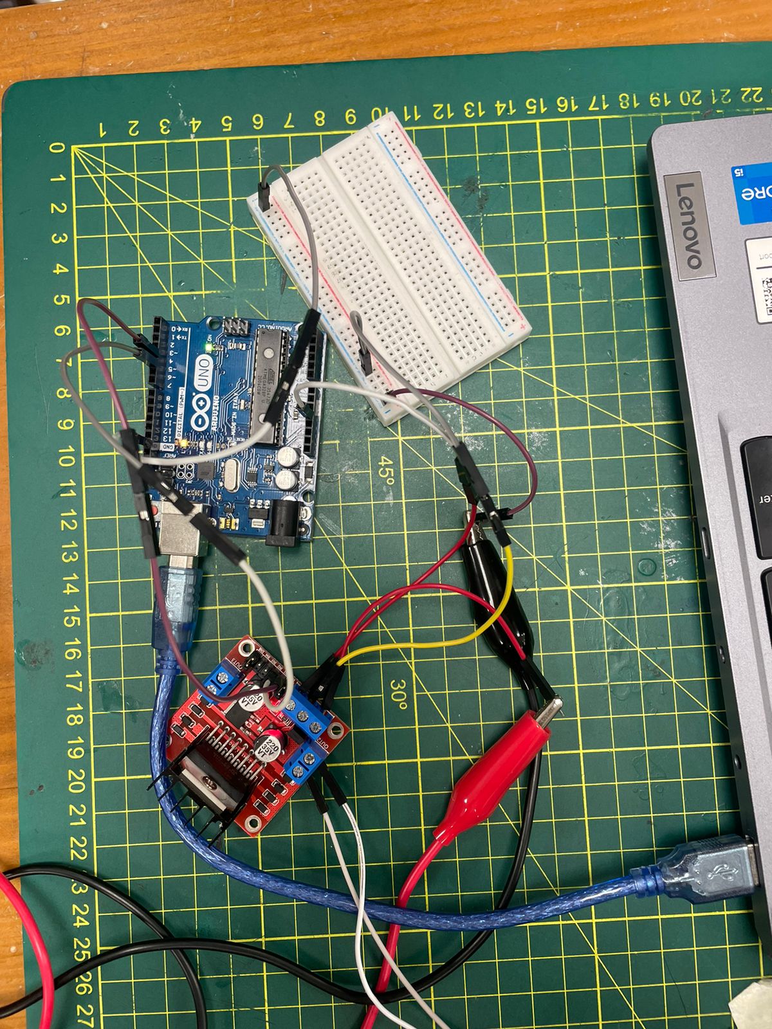
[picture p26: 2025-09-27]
Talleres/Taller 6/Motor DC - Conexiones.jpeg

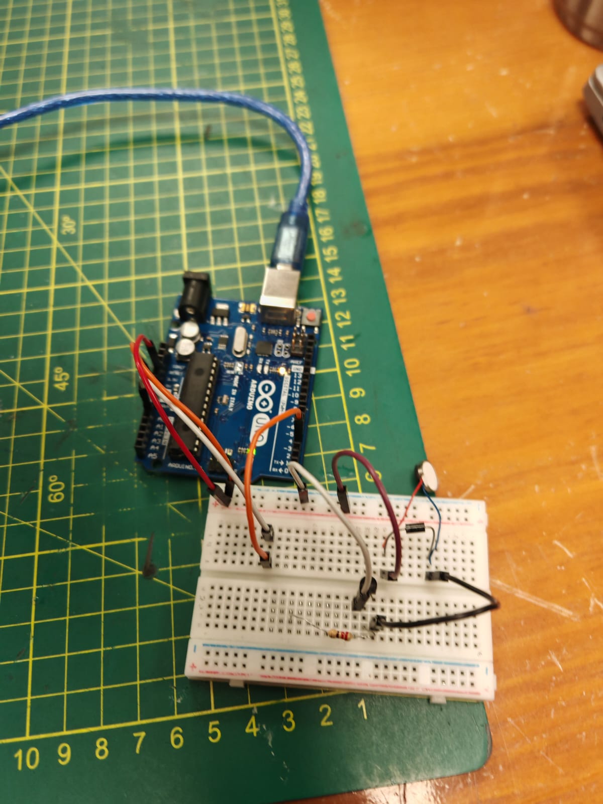
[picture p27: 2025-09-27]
Talleres/Taller 6/Microvibrador - Conexiones.jpeg

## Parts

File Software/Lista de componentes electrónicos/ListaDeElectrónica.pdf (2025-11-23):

Elementos electrónicos
Sensor de Fuerza FSR 406 | 1
Leds | 4
Step Up MT3608 | 1
Switch | 1
TP4056 USB C | 1
Batería de litio recargable 3.7V 2200mAh | 1
MPU 6050 | 1
ESP 32 | 1
Portabaterías | 1

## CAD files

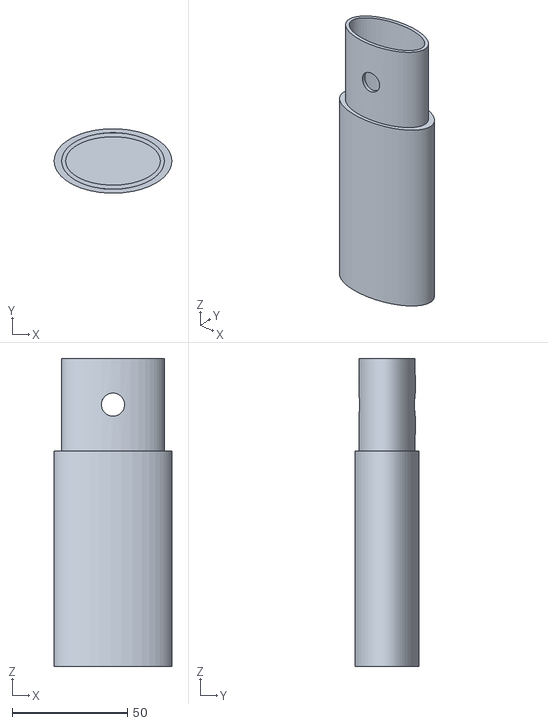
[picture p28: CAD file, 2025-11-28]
Hardware/Modelados 3D/Manillar v2.stl
51.0 x 27.9 x 133.5

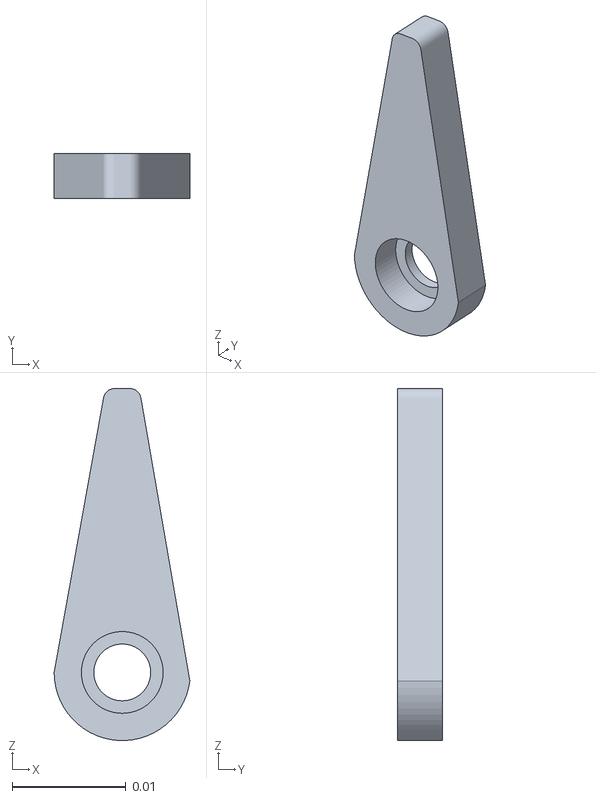
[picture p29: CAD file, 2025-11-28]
Hardware/Modelados 3D/Topes_Inferior.stl
0.012 x 0.004 x 0.031

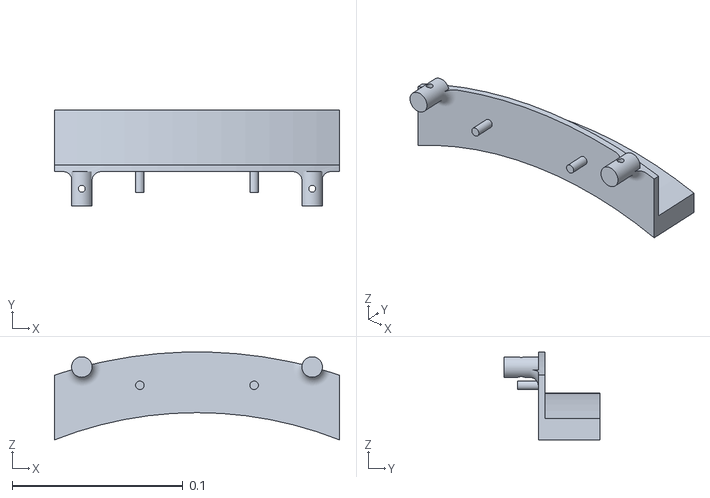
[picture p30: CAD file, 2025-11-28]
Hardware/Modelados 3D/Marco_Inferior.stl
0.167 x 0.056 x 0.0514

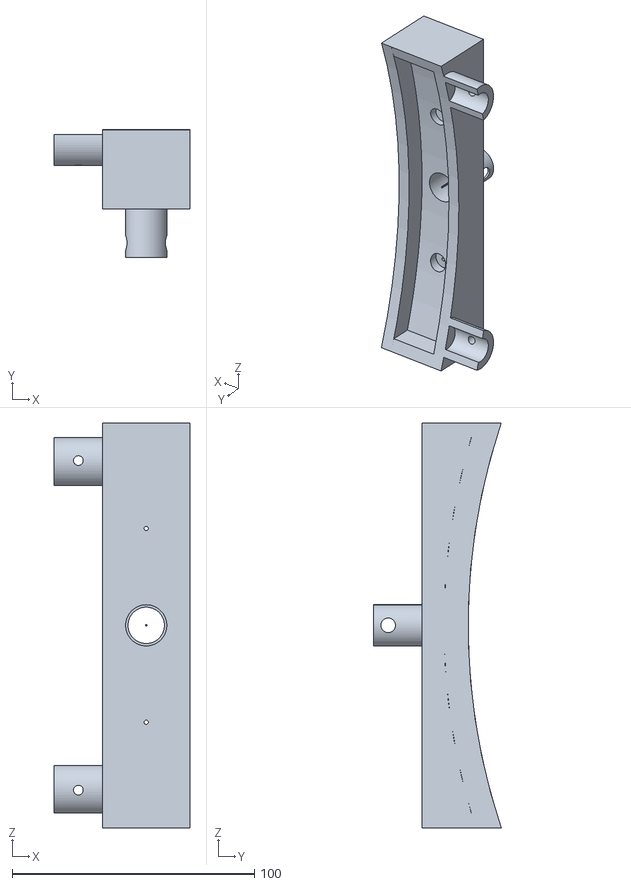
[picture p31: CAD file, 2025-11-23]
Hardware/Modelados 3D/Marco_Superior.stl
56.0 x 52.7 x 167.1

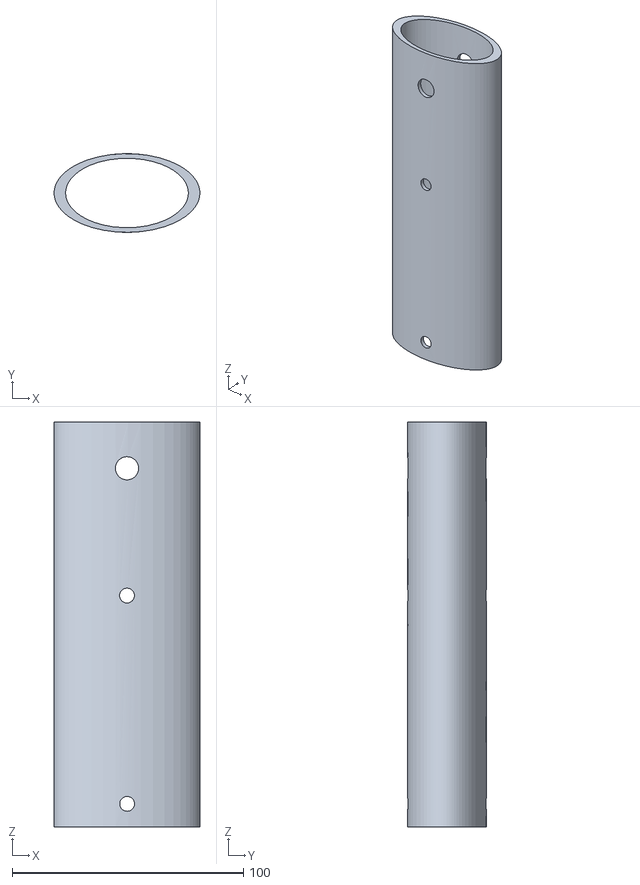
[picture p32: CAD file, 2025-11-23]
Hardware/Modelados 3D/Palanca_Exterior.stl
63.0 x 34.0 x 175.0

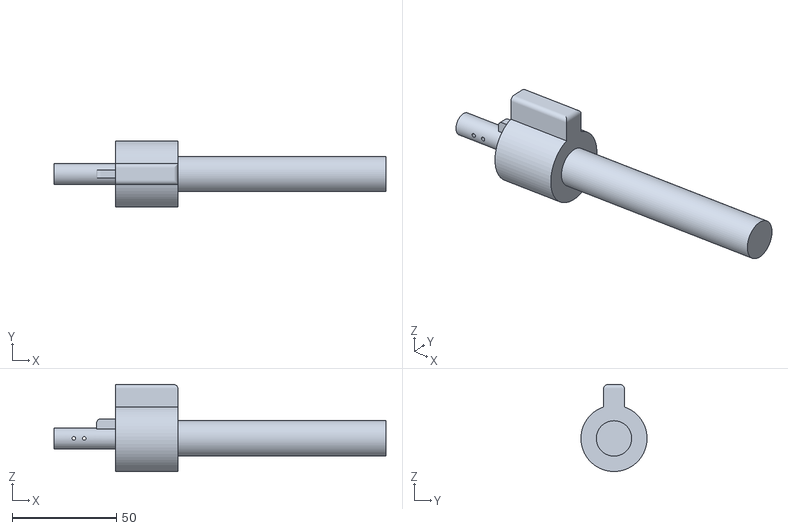
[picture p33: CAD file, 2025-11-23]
Hardware/Modelados 3D/Manillar_.stl
159.5 x 31.8 x 41.8

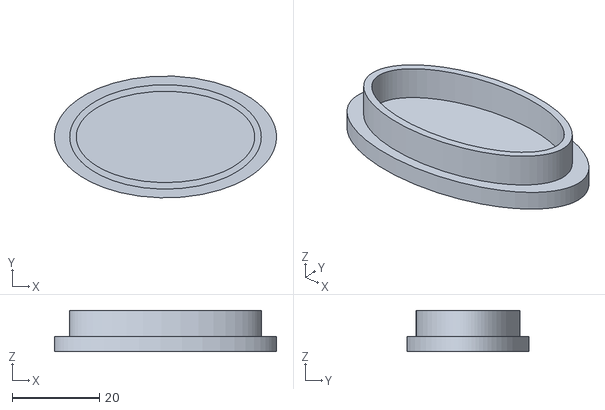
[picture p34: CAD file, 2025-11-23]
Hardware/Modelados 3D/Cubierta_Palanca.stl
51.0 x 27.9 x 9.50

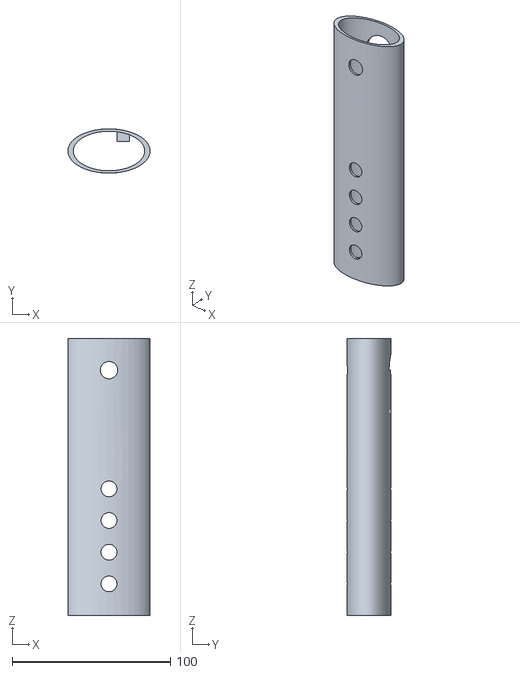
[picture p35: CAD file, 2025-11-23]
Hardware/Modelados 3D/Palanca_Interna.stl
52.0 x 28.0 x 175.0

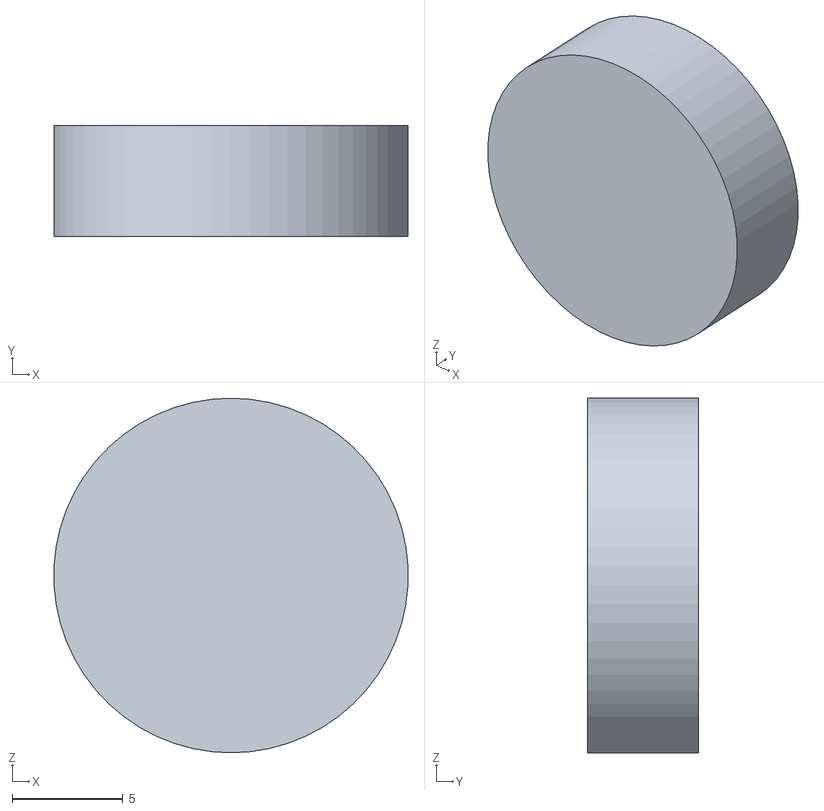
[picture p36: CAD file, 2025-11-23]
Hardware/Modelados 3D/Cubierta_Manillar.stl
16.0 x 5.00 x 16.0

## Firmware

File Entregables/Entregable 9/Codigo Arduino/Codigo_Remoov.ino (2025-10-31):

 // Librerias
#include "I2Cdev.h"
#include "MPU6050.h"
#include "Wire.h"
#include "BluetoothSerial.h"

// Crear objeto Bluetooth 
BluetoothSerial SerialBT;
MPU6050 sensor;

// Valores RAW del acelerometro
int16_t ax, ay, az;
const int fsrPin = 32, batteryPin= 34;    // Pin de FSR y lectura Nivel de batería
const float R1 = 100000.0, R2 = 50000.0;     // Resistencia superior e inferior (ohmios)
const float ADCmax = 4095.0;   // Resolución ADC ESP32 (12 bits)
const float Vref = 3.3;        // Voltaje de referencia ADC
const int ledCargado = 19, ledMedio = 18, ledBajo = 5, ledEncendido = 15;  // LEDs de bateria
float angMin = 9999, angMax = -9999, radio = 0.15;
unsigned long lastMeasureTime = 0;  // Tiempo de última medición
const unsigned long interval = 20000;  // 20 segundos

// --- FUNCIÓN PARA LEER Y CLASIFICAR ESTADO DE BATERÍA ---
float readBatteryVoltage() {
  int raw = analogRead(batteryPin);
  float v_adc = (raw / ADCmax) * Vref;            // Voltaje en el pin ADC
  float v_bat = v_adc * (R1 + R2) / R2;           // Corrige por divisor
  return v_bat;
}

int batteryStatus(float v_bat) {
  if (v_bat >= 4.0) return 3;
  else if (v_bat >= 3.7) return 2;
  else if (v_bat >= 3.5) return 1;
  else return 0;
}
void updateBatteryLEDs(int estado) {
  digitalWrite(ledCargado, LOW);
  digitalWrite(ledMedio, LOW);
  digitalWrite(ledBajo, LOW);

  if (estado == 3) digitalWrite(ledCargado, HIGH);
  else if (estado == 2) digitalWrite(ledMedio, HIGH);
  else digitalWrite(ledBajo, HIGH);
}

void setup() {
  Serial.begin(9600);   
  Wire.begin();           //Iniciando I2C  
  SerialBT.begin("ESP32");
  sensor.initialize();    //Iniciando el sensor

  if (sensor.testConnection()) Serial.println("Sensor iniciado correctamente");
  else Serial.println("Error al iniciar el sensor");

  // pines
  pinMode(fsrPin, INPUT);
  pinMode(ledCargado, OUTPUT);
  pinMode(ledMedio, OUTPUT);
  pinMode(ledBajo, OUTPUT);
  pinMode(ledEncendido, OUTPUT);
}

void loop() {
  // Leer voltaje de batería
  float vbat = readBatteryVoltage();
  int estadoBat = batteryStatus(vbat);

  // Mostrar por monitor serial
  Serial.print("Batería: ");
  Serial.print(vbat, 2);
  Serial.print(" V  Estado: ");
  Serial.println(estadoBat);
  // ---- Actualizar LEDs según estado ----
  updateBatteryLEDs(estadoBat); 
  
  // Leer las aceleraciones 
  sensor.getAcceleration(&ax,&ay,&az);
  //Calcular los angulos de inclinacion:
  float accel_ang_x=atan(ax/sqrt(pow(ay,2) + pow(az,2)))*(180.0/3.14)+90;
  float accel_ang_y=atan(ay/sqrt(pow(ax,2) + pow(az,2)))*(180.0/3.14)+90;
  // --- Actualizar ángulos extremos ---
  if (accel_ang_x < angMin) angMin = accel_ang_y;
  if (accel_ang_x > angMax) angMax = accel_ang_y;

  int fsrValue = analogRead(fsrPin)/100;

  //Mostrar angulos y fuerza
  Serial.print("Inclinacion en X: ");
  Serial.print(accel_ang_x); 
  Serial.print(" Inclinacion en Y:");
  Serial.println(accel_ang_y);
  Serial.print("FSR: ");
  Serial.println(fsrValue);
  

  // Enviar por Bluetooth
  SerialBT.print(fsrValue); 
  SerialBT.print("?");
  SerialBT.print(accel_ang_y);
  SerialBT.print("?");
  SerialBT.println(estadoBat);
  SerialBT.print("?");
  if (millis() - lastMeasureTime >= interval) {
    float deltaAng = abs(angMax - angMin);         // Diferencia angular (°)
    float arco = radio * (deltaAng * PI / 180.0);  // Longitud del arco (m)
    Serial.print("Longitud del arco: ");
    Serial.print(arco, 3);
    Serial.println(" m");

    SerialBT.println(arco, 3);

    // Reiniciar medición
    angMin = 9999;
    angMax = -9999;
    lastMeasureTime = millis();
  }
  
  if (SerialBT.available()) {
    String dato = SerialBT.readStringUntil('\n');  // Leer hasta salto de línea
    dato.trim();  // Elimina espacios o retornos
    float nuevoRadio = dato.toFloat();
    if (nuevoRadio > 0) { 
      radio = nuevoRadio;
      Serial.print("Nuevo radio recibido: ");
      Serial.print(radio);
      Serial.println(" m");
    }
  }
  delay(500);
}
